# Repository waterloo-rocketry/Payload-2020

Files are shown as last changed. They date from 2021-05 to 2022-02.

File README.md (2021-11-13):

# Waterloo Rocketry Payload 2020/2021

Waterloo Rocketry's Payload hardware and software for the radiation materials analysis experiment

## Contents

PCB Hardware and embedded software for:
* Papa board (power management, logging)
* Mama board (particle detection, noise filtering)
* Protoboard (Mama board prototype board)

Geant4 Monte Carlo simulations have been moved to Payload-Sims

Software for the in-flight controller (see [firmware readme](controller_firmware/README.md))

## Prerequisites

* KiCad
* Geant4
	* See [this link](http://geant4-userdoc.web.cern.ch/geant4-userdoc/UsersGuides/InstallationGuide/html/index.html) for more information on setting up the Geant4 environment
* STM32CubeIDE (see [firmware readme](controller_firmware/README.md))

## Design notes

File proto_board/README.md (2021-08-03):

***************************************Protoboard**************************************

Two parts:

	detector_support:
		* All the supporting infastrucutre, power suppies, logging
	detector_circuit
		* Converts current spike from SiPM to voltage for logging.
			* detector_circuit_LTC6269.sch - Version with LTC6269 op amp. 
			  this amp has been tested and works, but is expensive and consumes 
                          a lot of current, not ideal for flight.
		* detector_circuit_LTC6254 - Version with LTC6264 op amp, previously untested
                  but cheaper and has a significantly lower quiescent current.
		* detector_circuit_alt_LTC6254 - Different version of transimpedance amplifier with 
		  filtering built in. Experimental, but it would be really cool and worth a try. 

Each of the detector circuits connect to the support board with the listed connectors:
* J9 - SIPM_CONN
* J2 - DET_CONN_PWR
* J11 

***********************************Project Overview***********************************

Measuring the radiation detection properties of BNNTs and Metal Oxides.

Radiaiton detection
Scintillator - Lights up when exposed to ionizing radiation
SiPM - Silicon photomultiplier, sensor that counts the number of photons it sees.

Scintillator generates light, SiPM generates a current pulse proportional 
to the magnitude of radiation.

In order to detect and log that current pulse on an MCU we need to
1. Convert the current signal to voltage 
2. Amplify the voltage pulse to increase difference between singal and noise
and make it easier to detect and losses negligible.
3. Extend the length of the signal so the MCU has time to made an ADC conversion.

Detector Circuit Topology:

1. Transimpdance amplifier converts current signal to voltage, amplifies it in a way
to reduce the signal to noise ratio. The main purpose of this board is to fine-tune the 
resistor and capacitor values to optimize the gain on this amplifier.
2. Filter stage to eliminaty high and low frequency noise
3. Second stage amplfication
4. Peak detector to extend signal
5. Voltage follower to ensure signal sampling does not interfere with the peak detector circuit.

Data logging:

After the second stage amplificaiton, the signal line is sent to both the peak detector and a comparator.
The comparator compares the signal to a set baseline voltage value, and if the signal exceeds this amount,
it generates an interrupt. This interrupt is used to tell the MCU when to take an ADC sample from the 
peak detector line. 

Voltage supply:

Because the detector circuit is sensative anlaog circuitry, it runs off a seperate 4.7V line 
from an LDO. The LDO cleans the 5V line to ensure low-noise, as well as seperates the detector
circuit supplies from any noise generated by the switching supplies.

The SiPM requires 36V to operate. This is achieved with a voltage booster paried with an LDO to 
make sure the supply voltage is clean. 

The detector_support circuit is configured to support both a test connection (5V and 12V from the 
bench top supply) as well as battery connections for use in lab testing.

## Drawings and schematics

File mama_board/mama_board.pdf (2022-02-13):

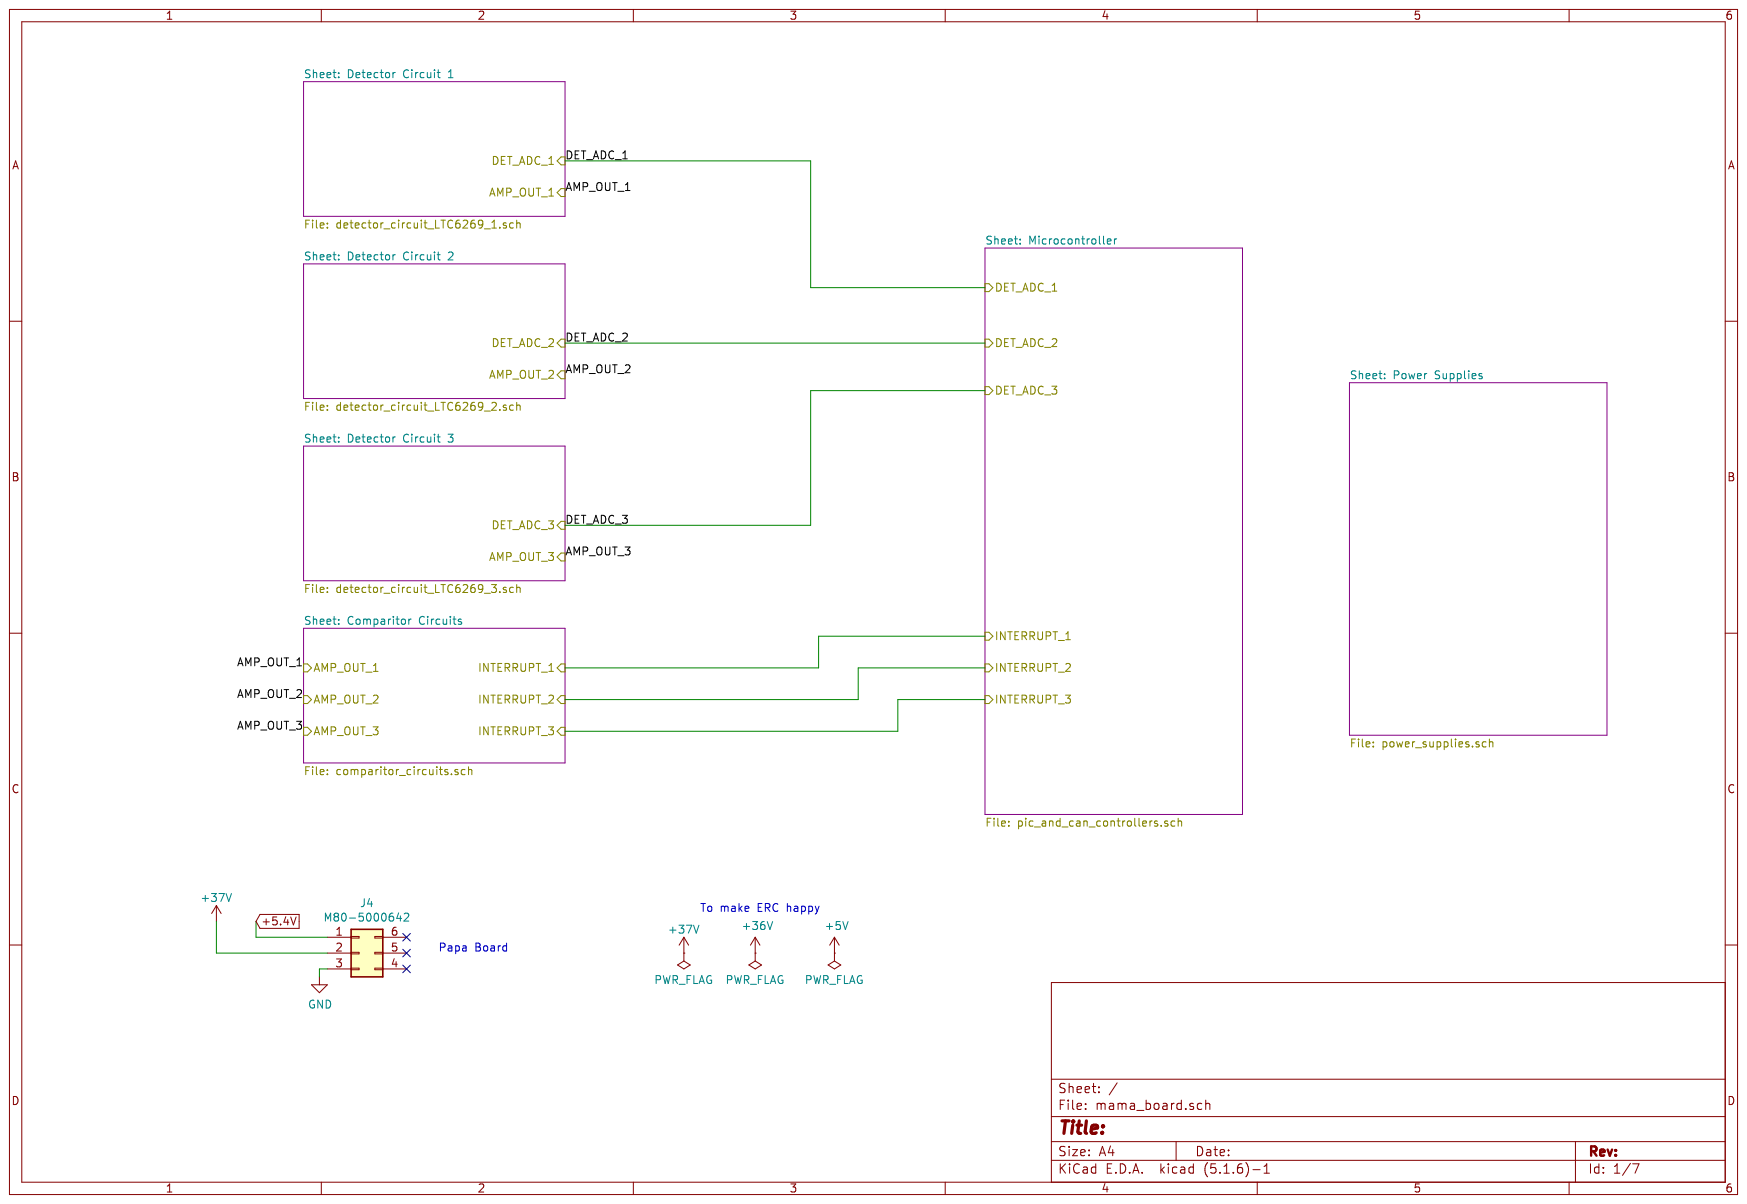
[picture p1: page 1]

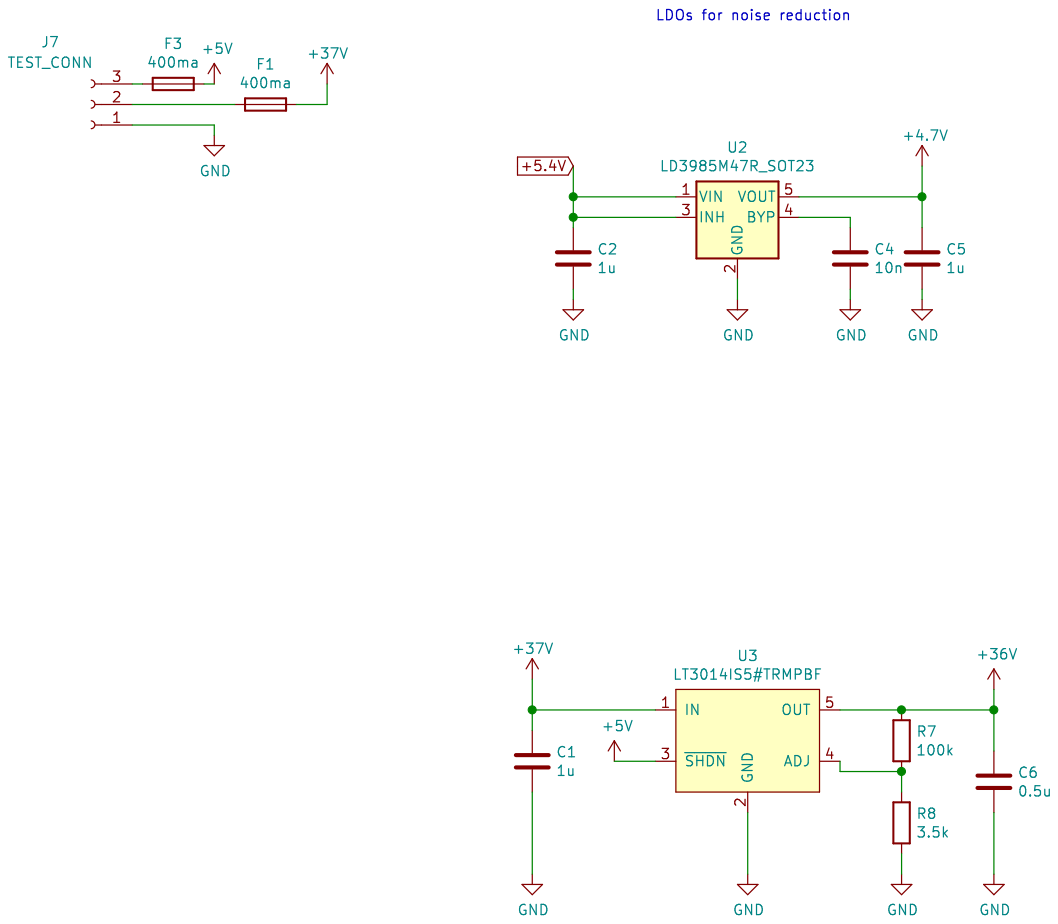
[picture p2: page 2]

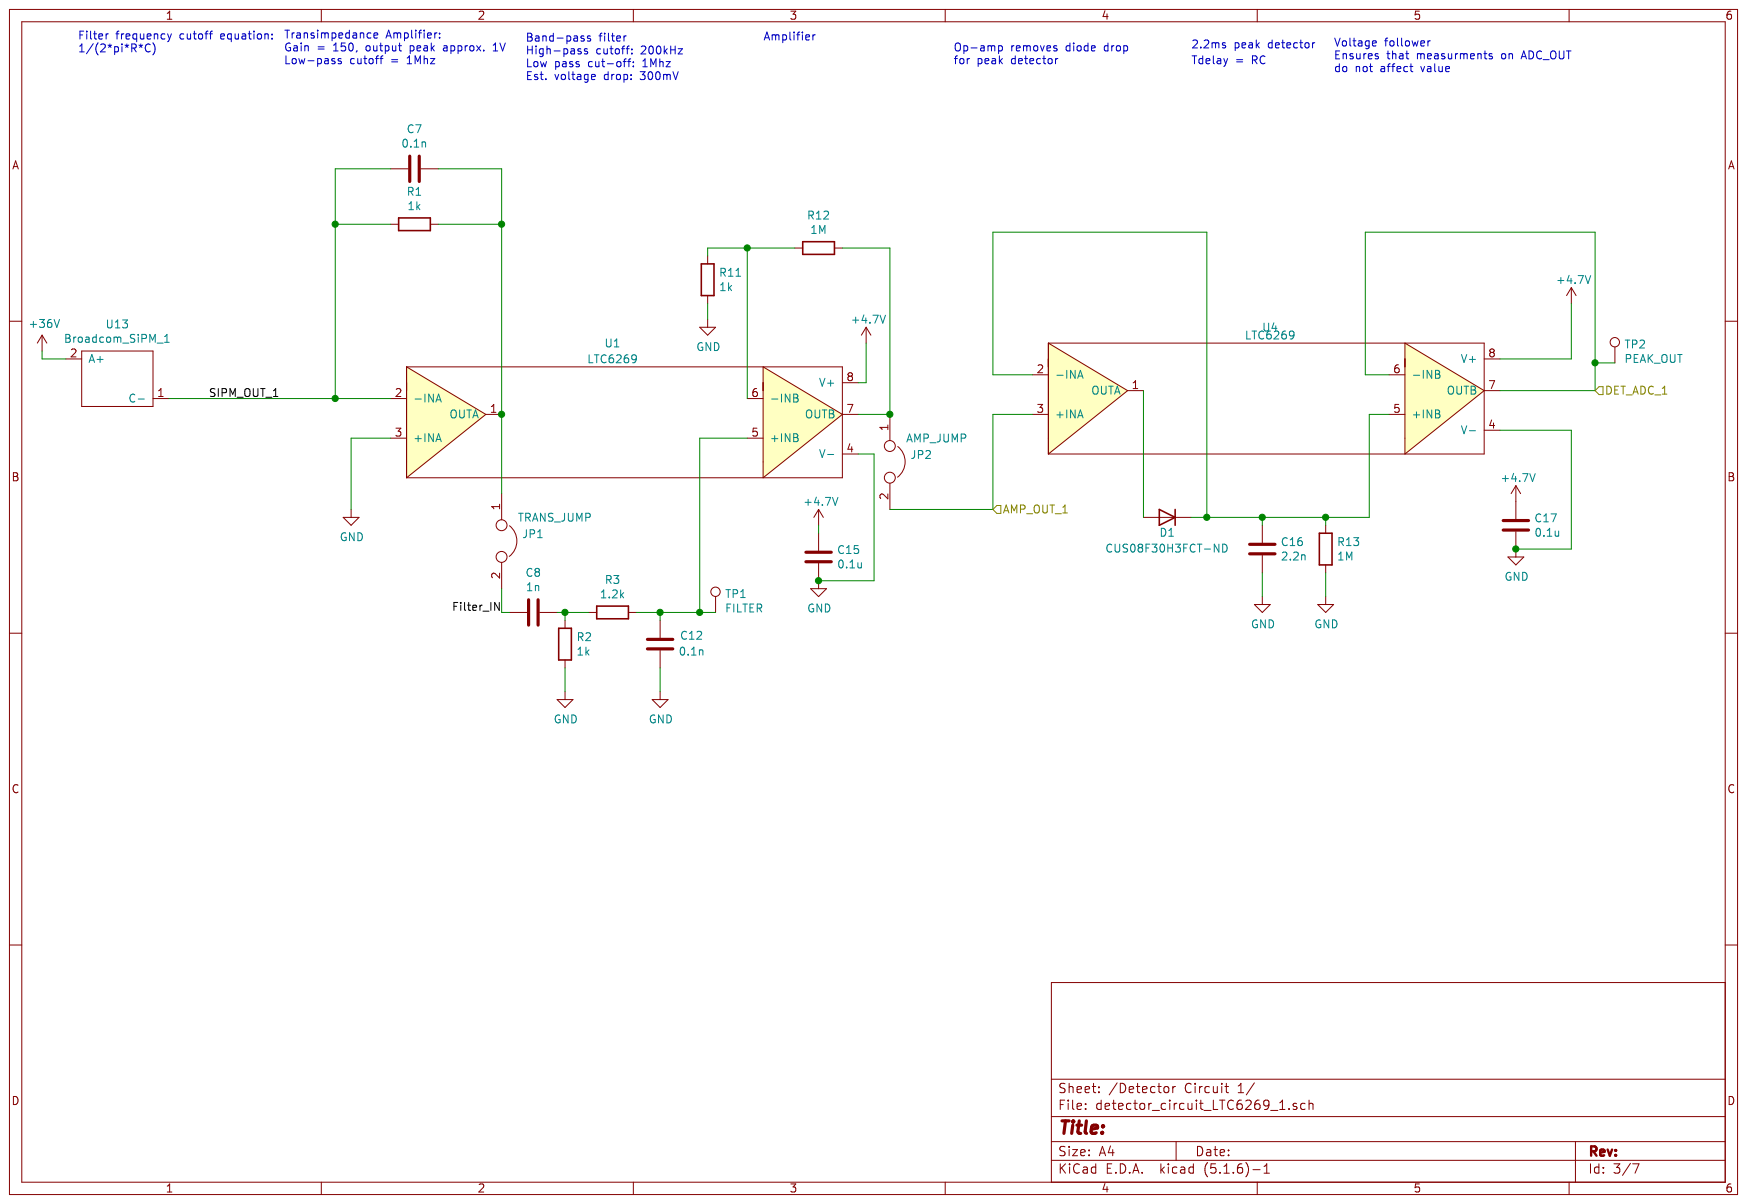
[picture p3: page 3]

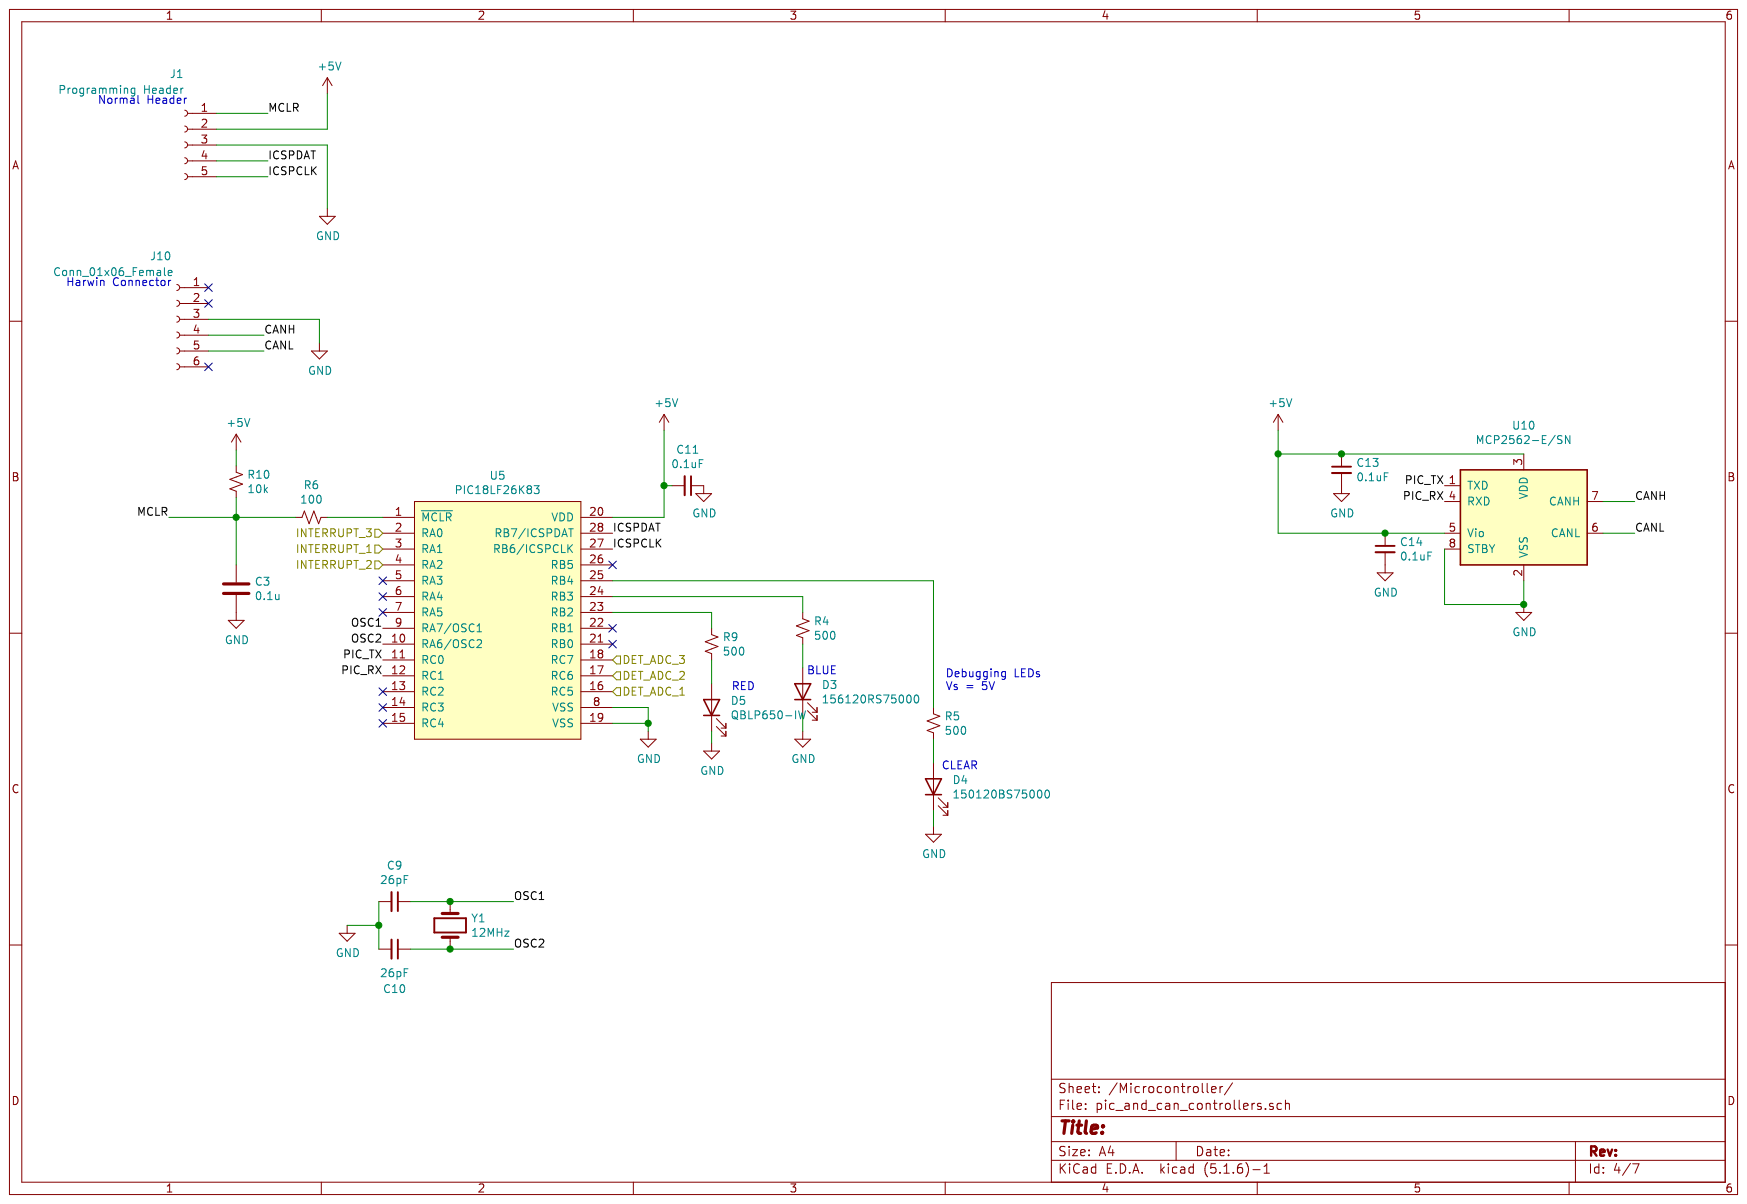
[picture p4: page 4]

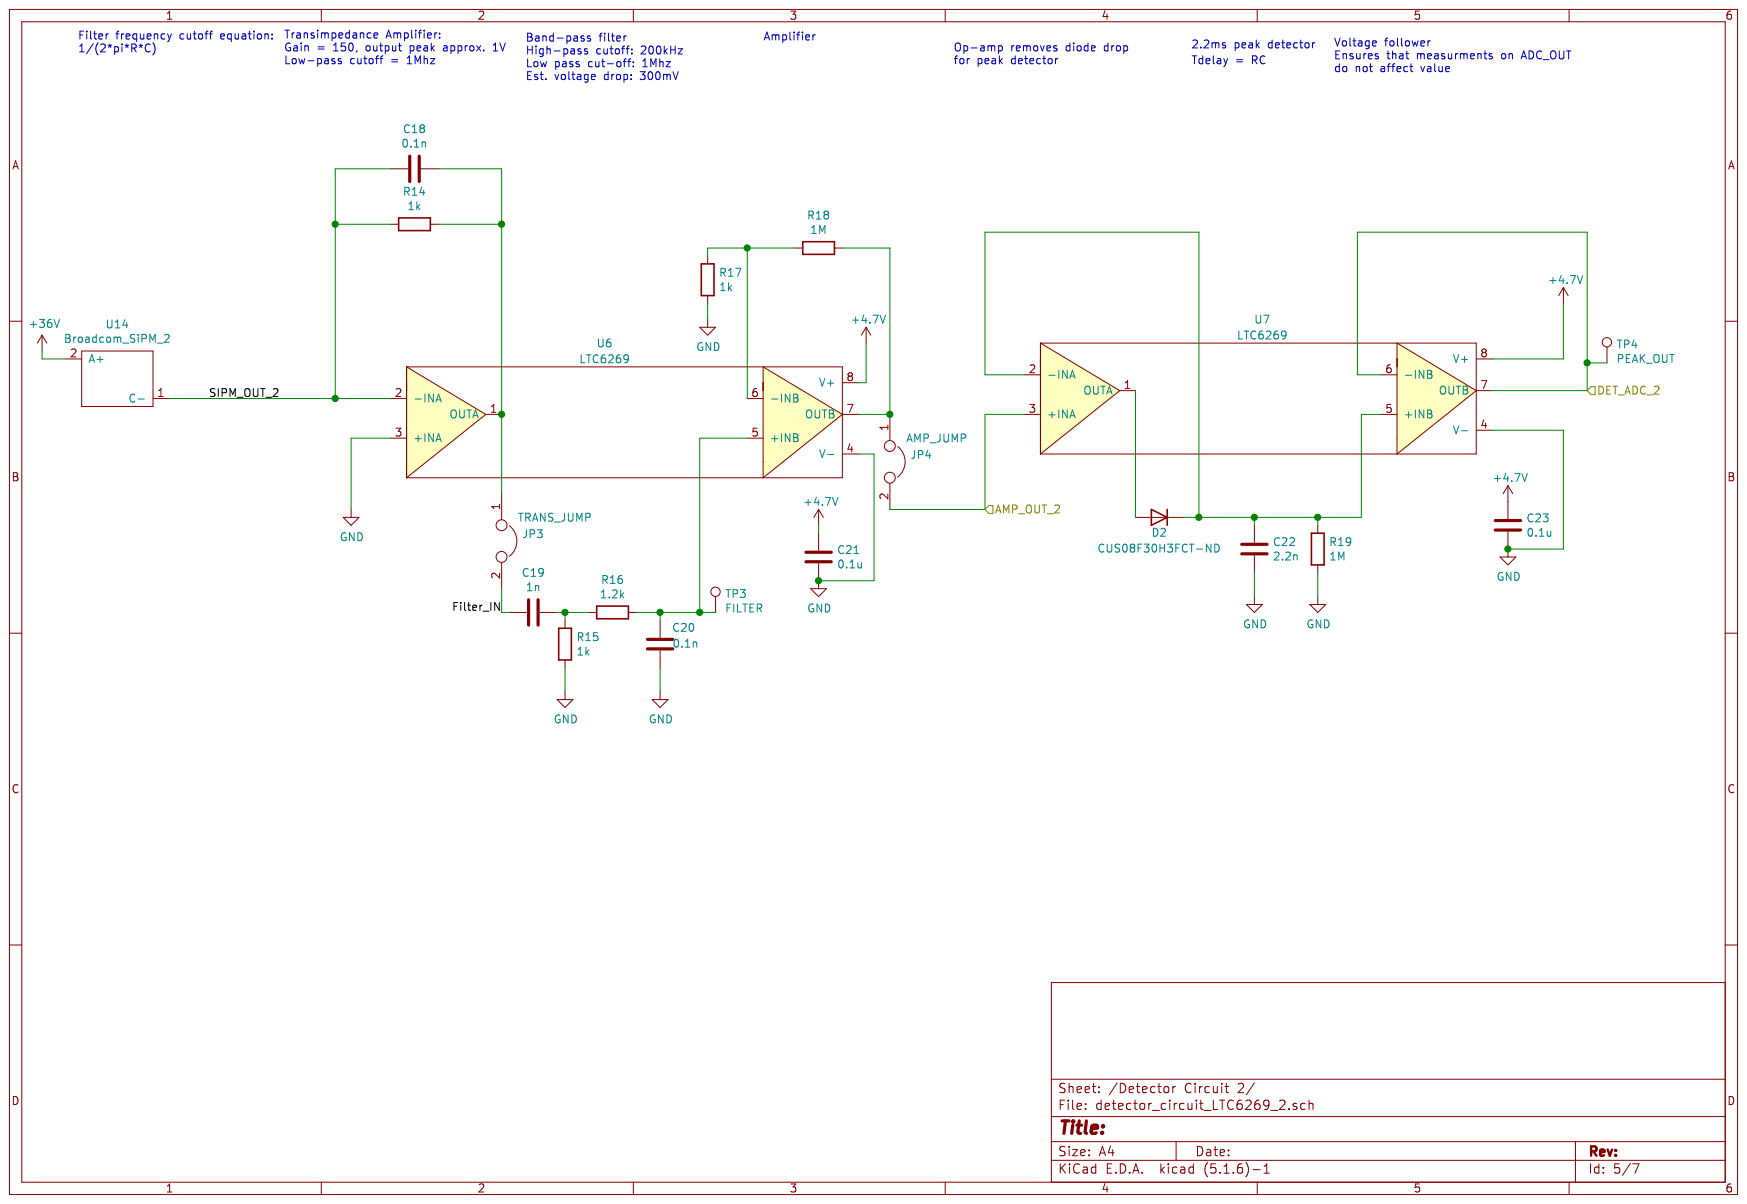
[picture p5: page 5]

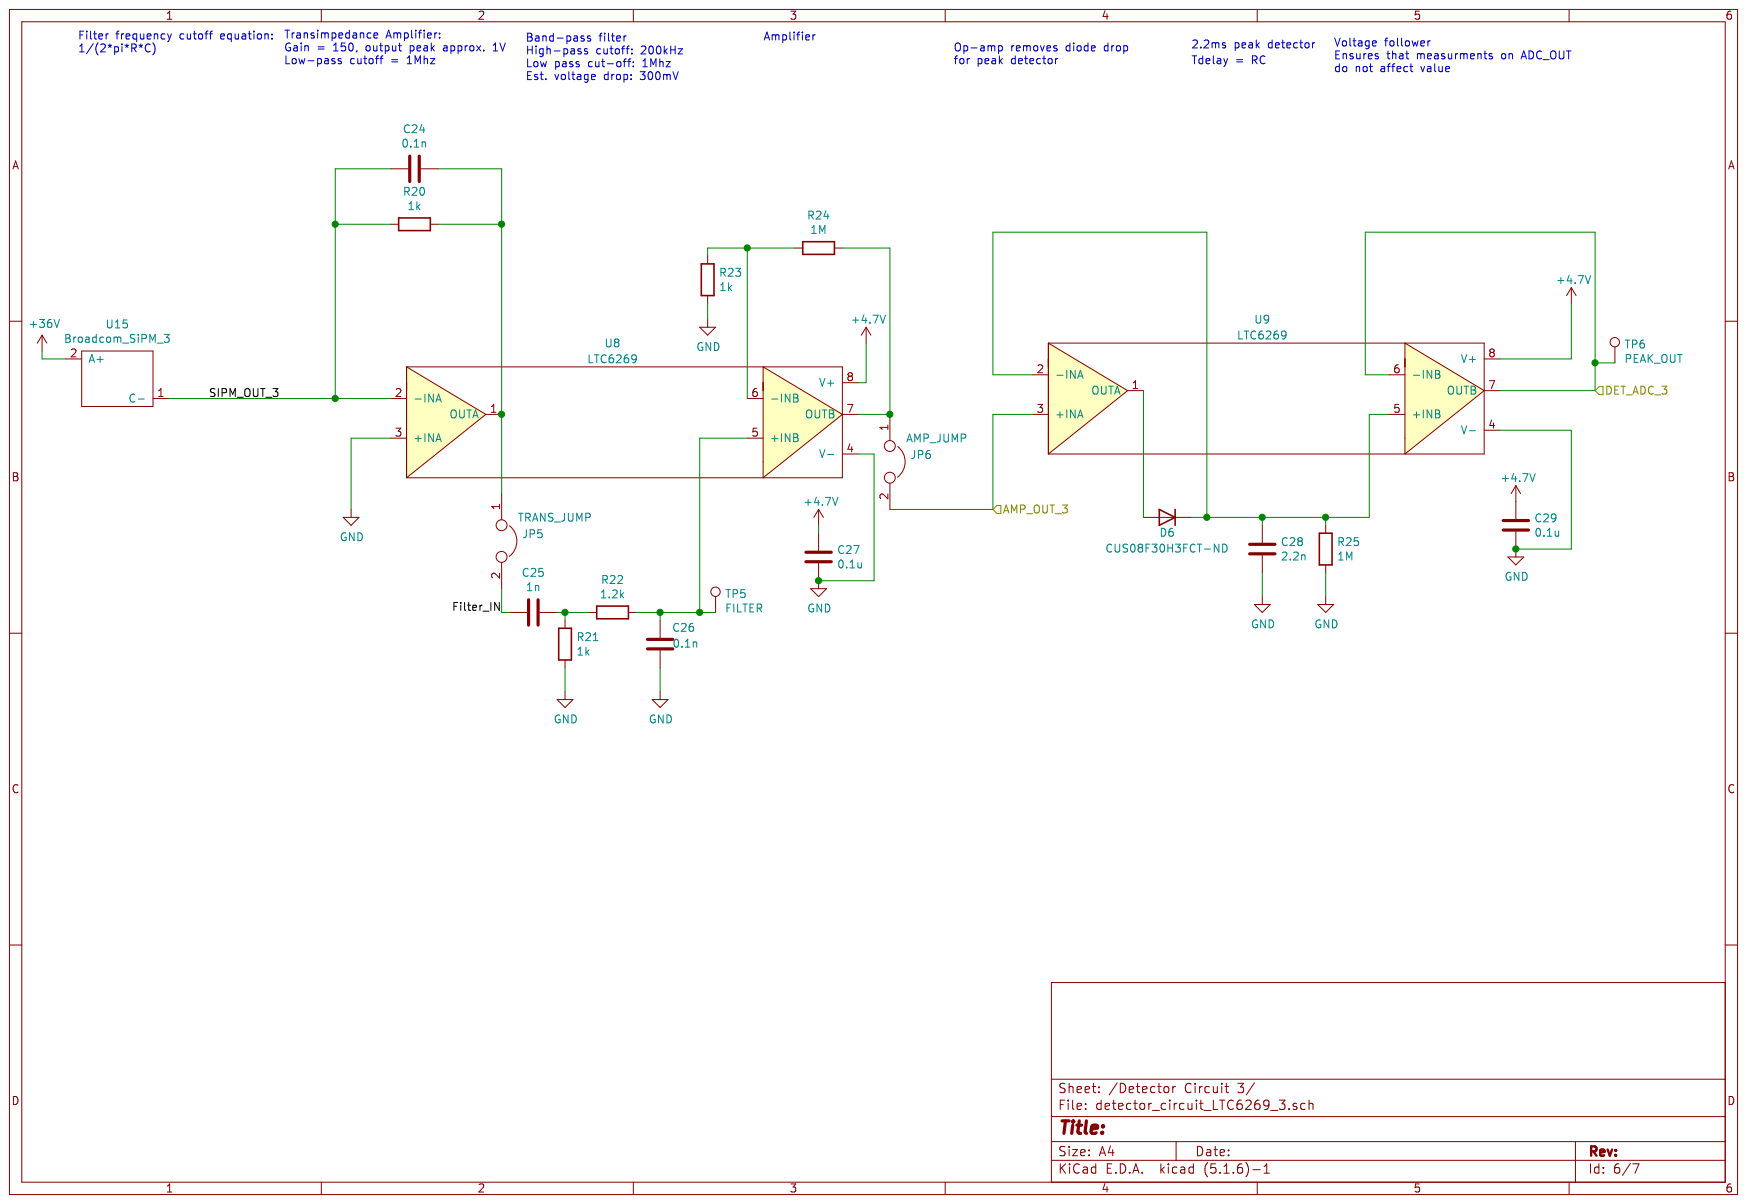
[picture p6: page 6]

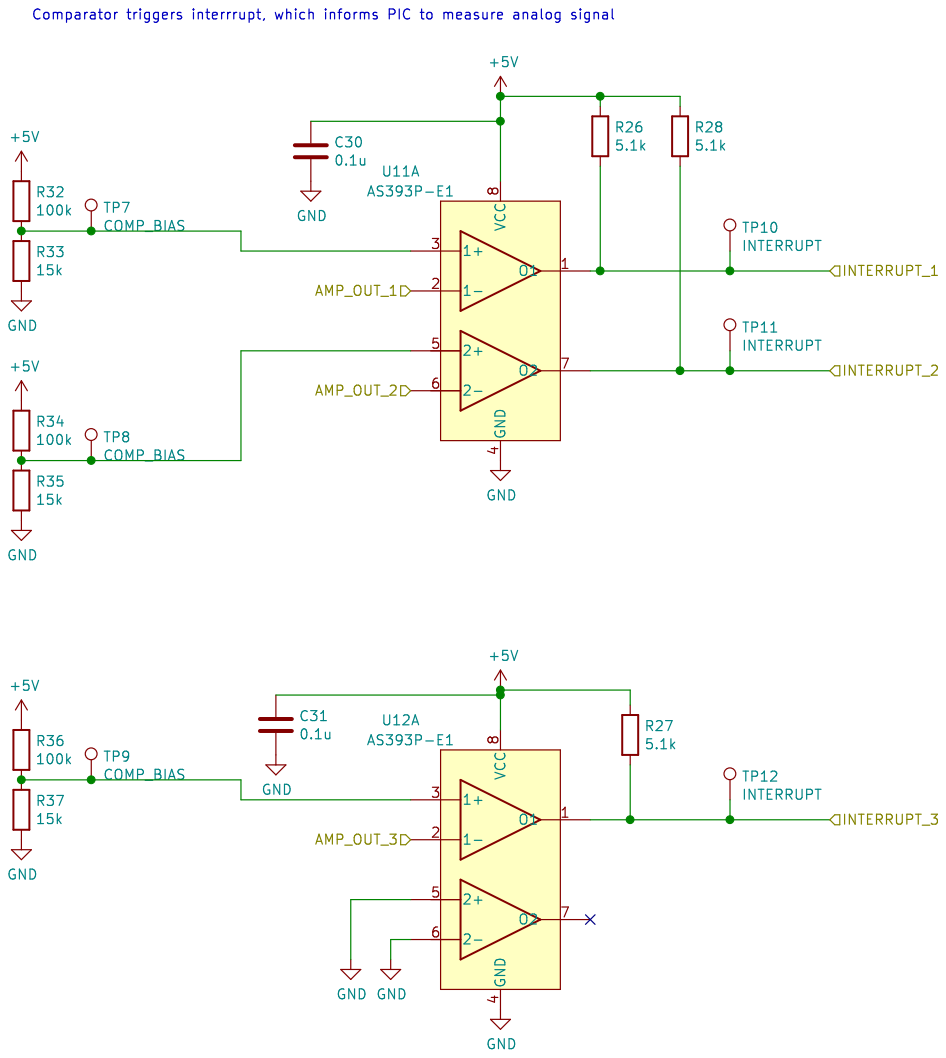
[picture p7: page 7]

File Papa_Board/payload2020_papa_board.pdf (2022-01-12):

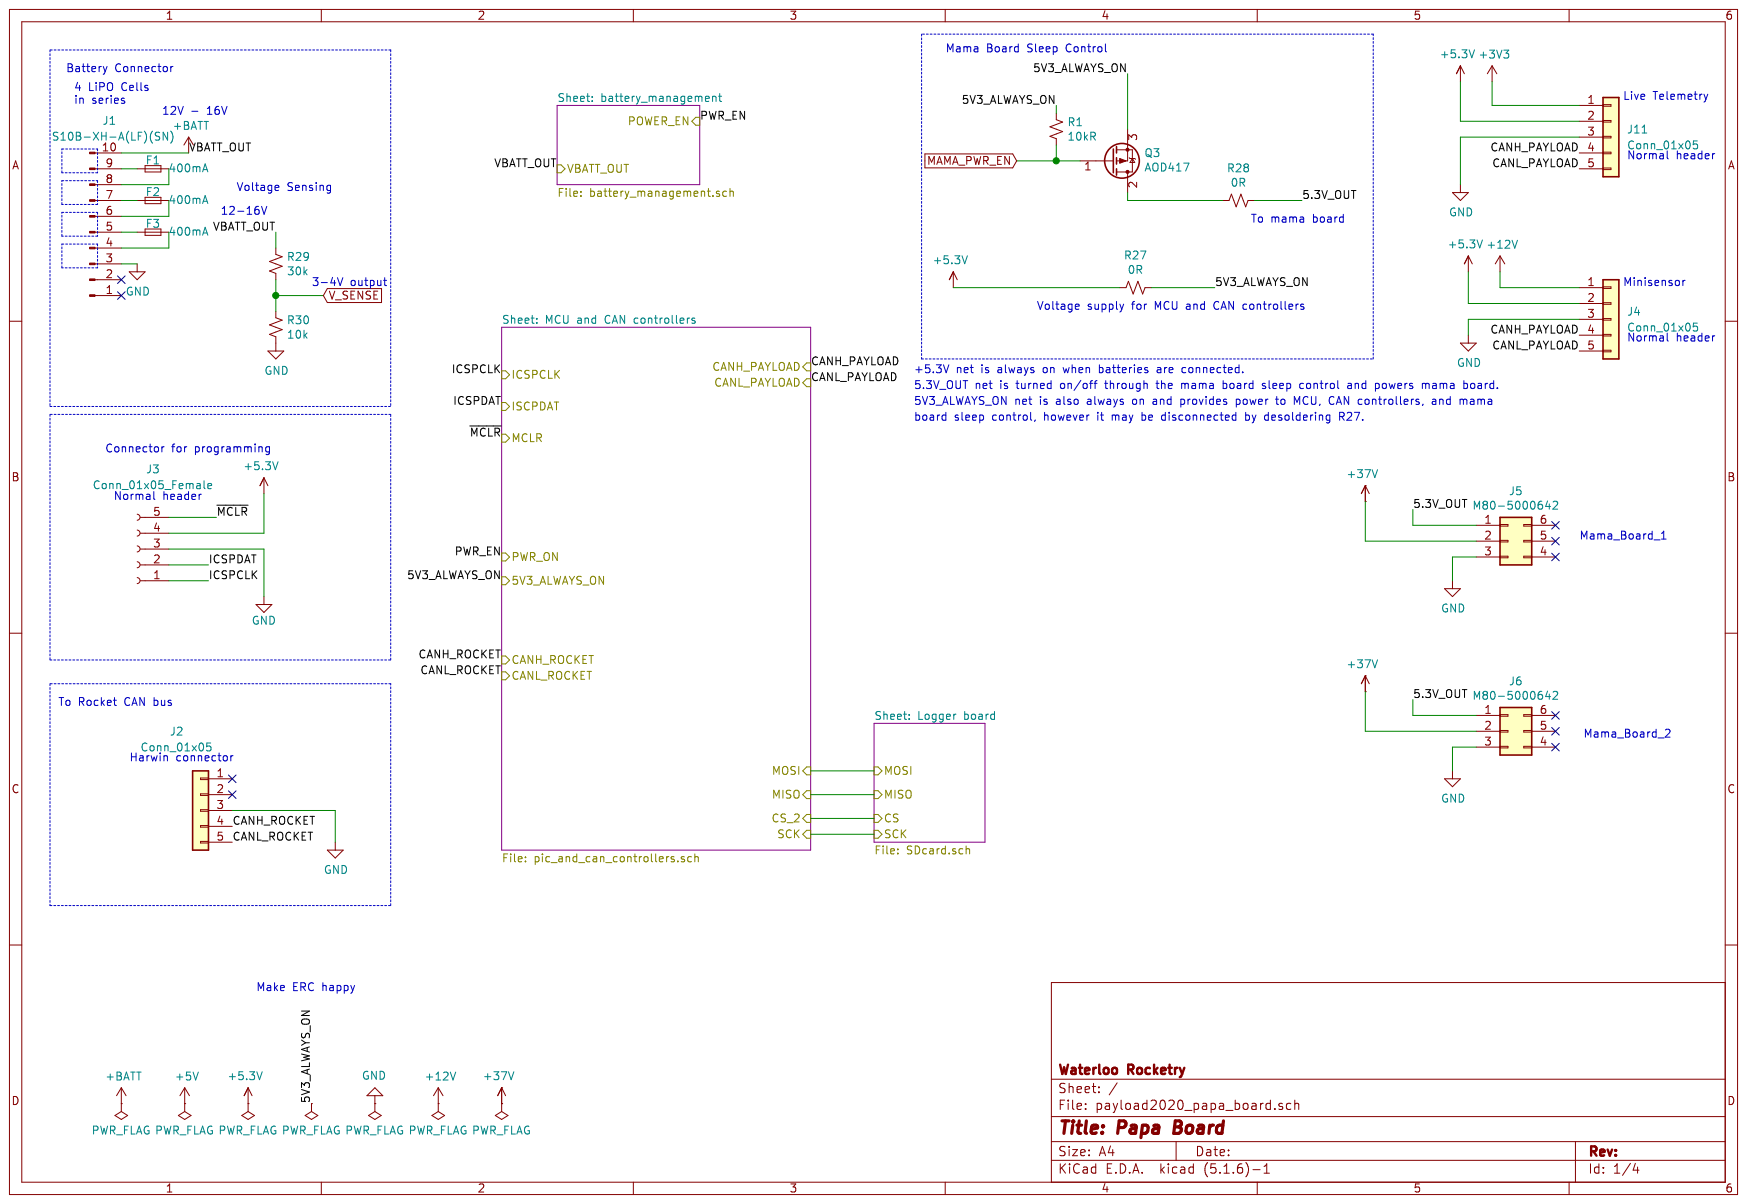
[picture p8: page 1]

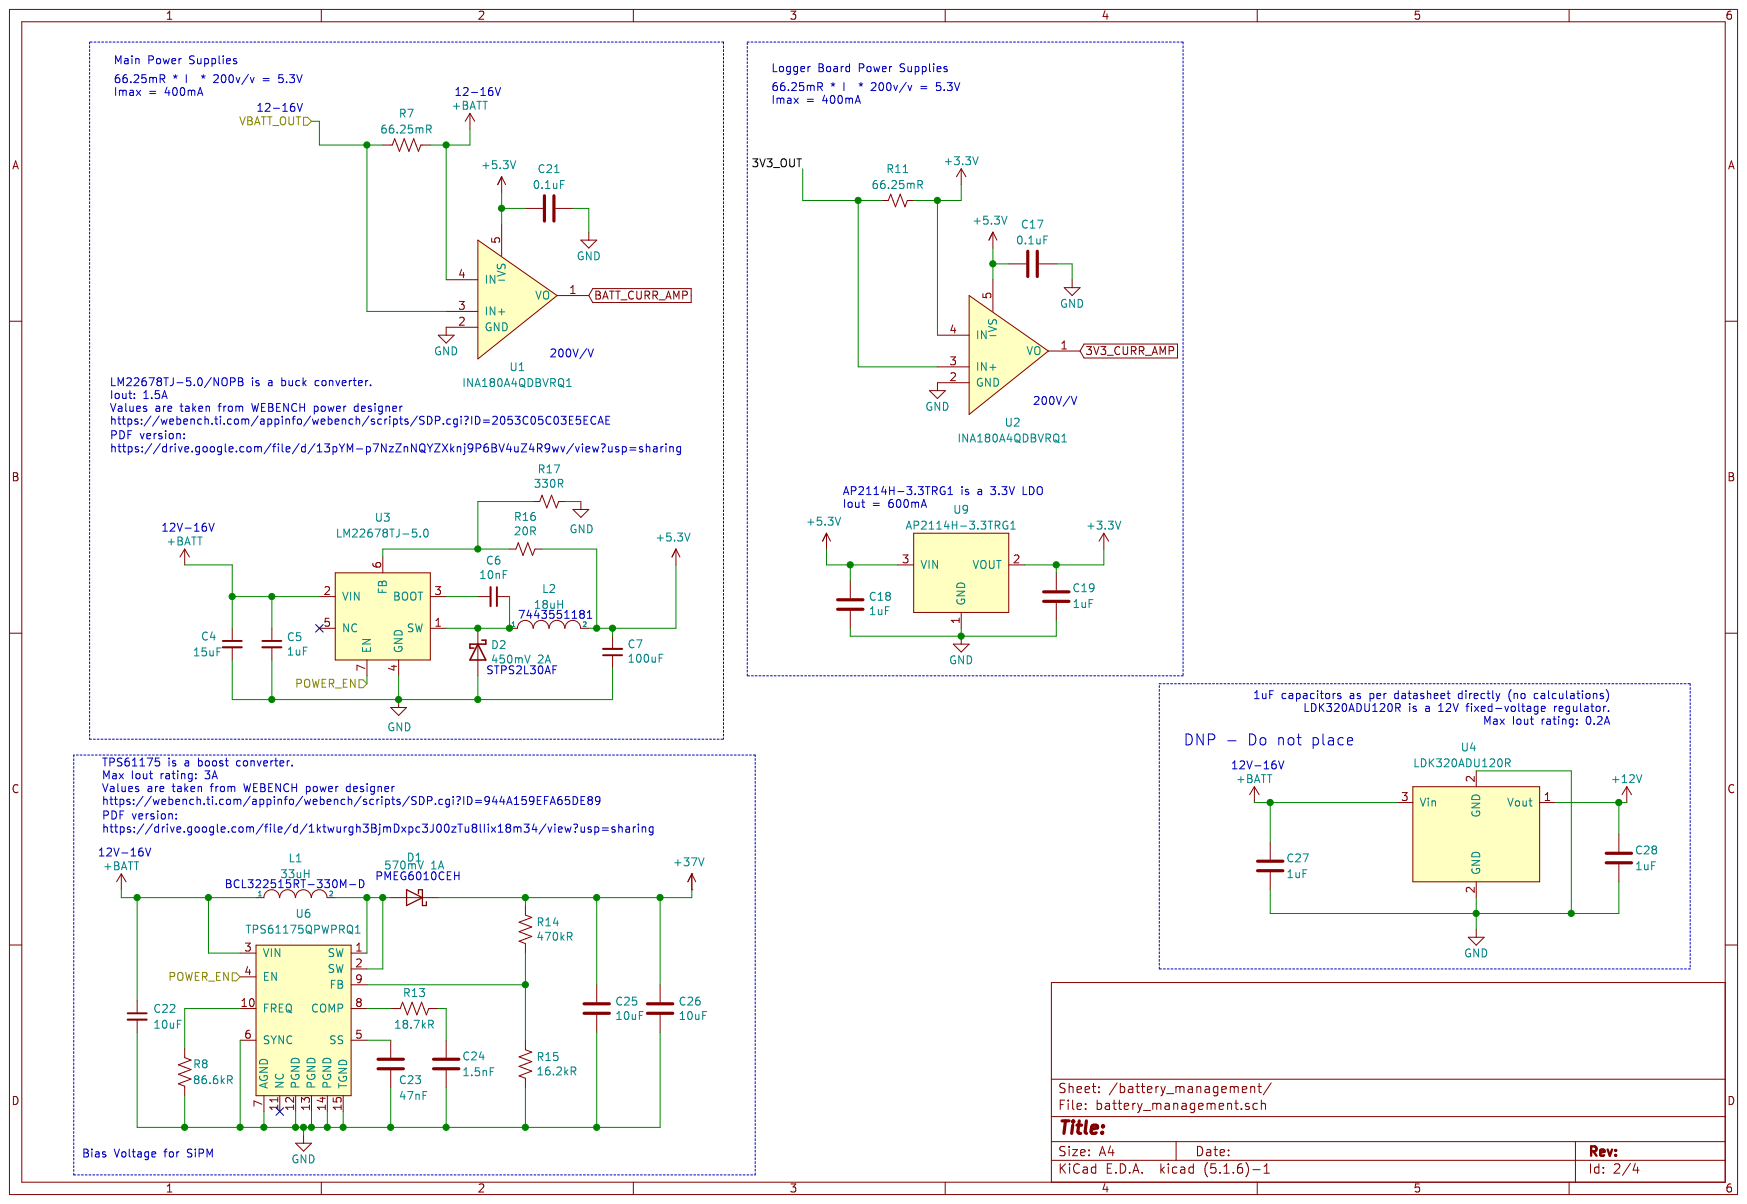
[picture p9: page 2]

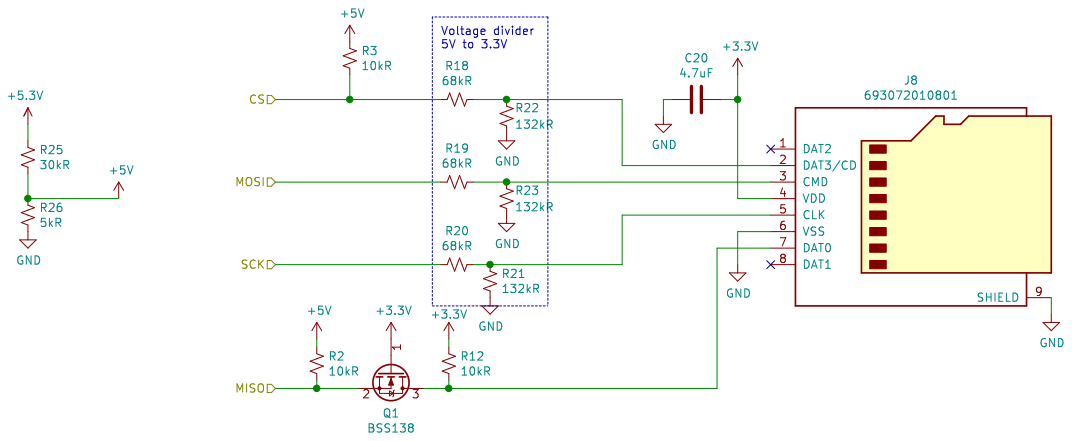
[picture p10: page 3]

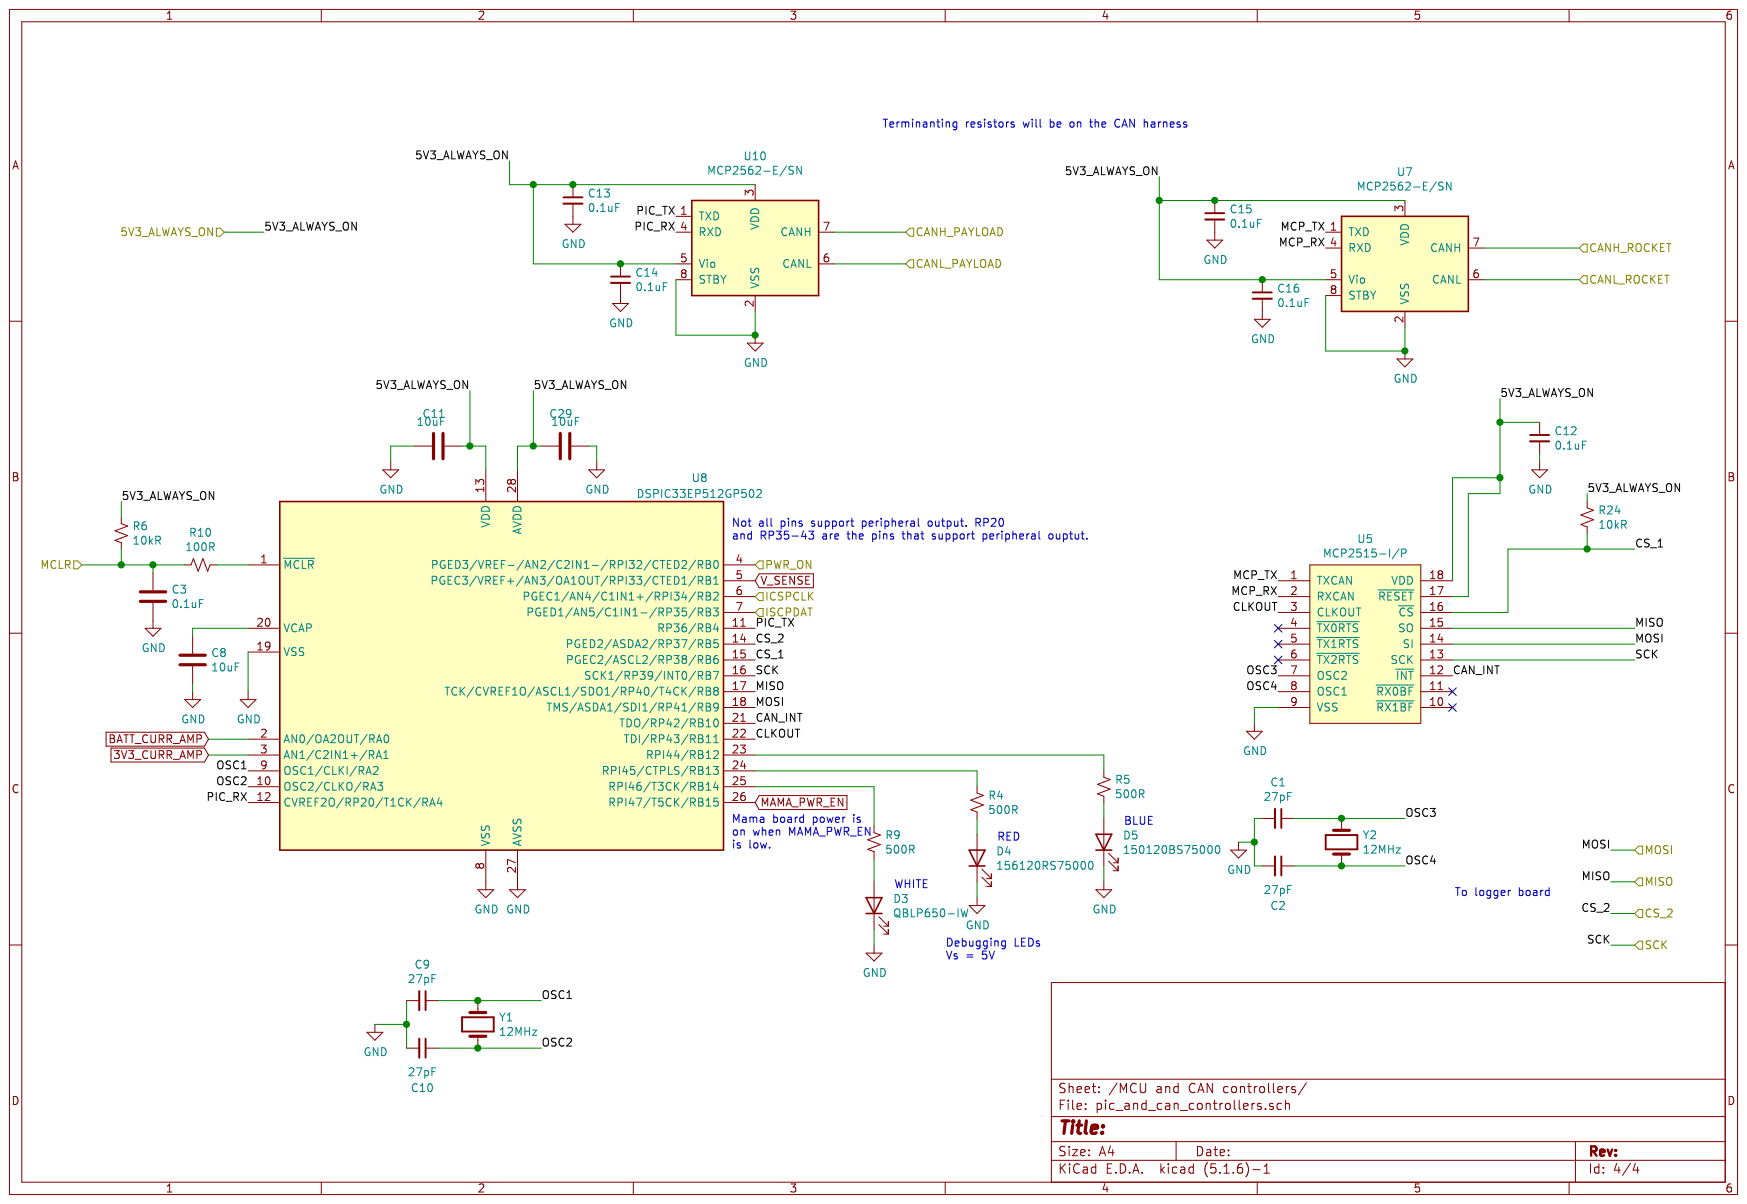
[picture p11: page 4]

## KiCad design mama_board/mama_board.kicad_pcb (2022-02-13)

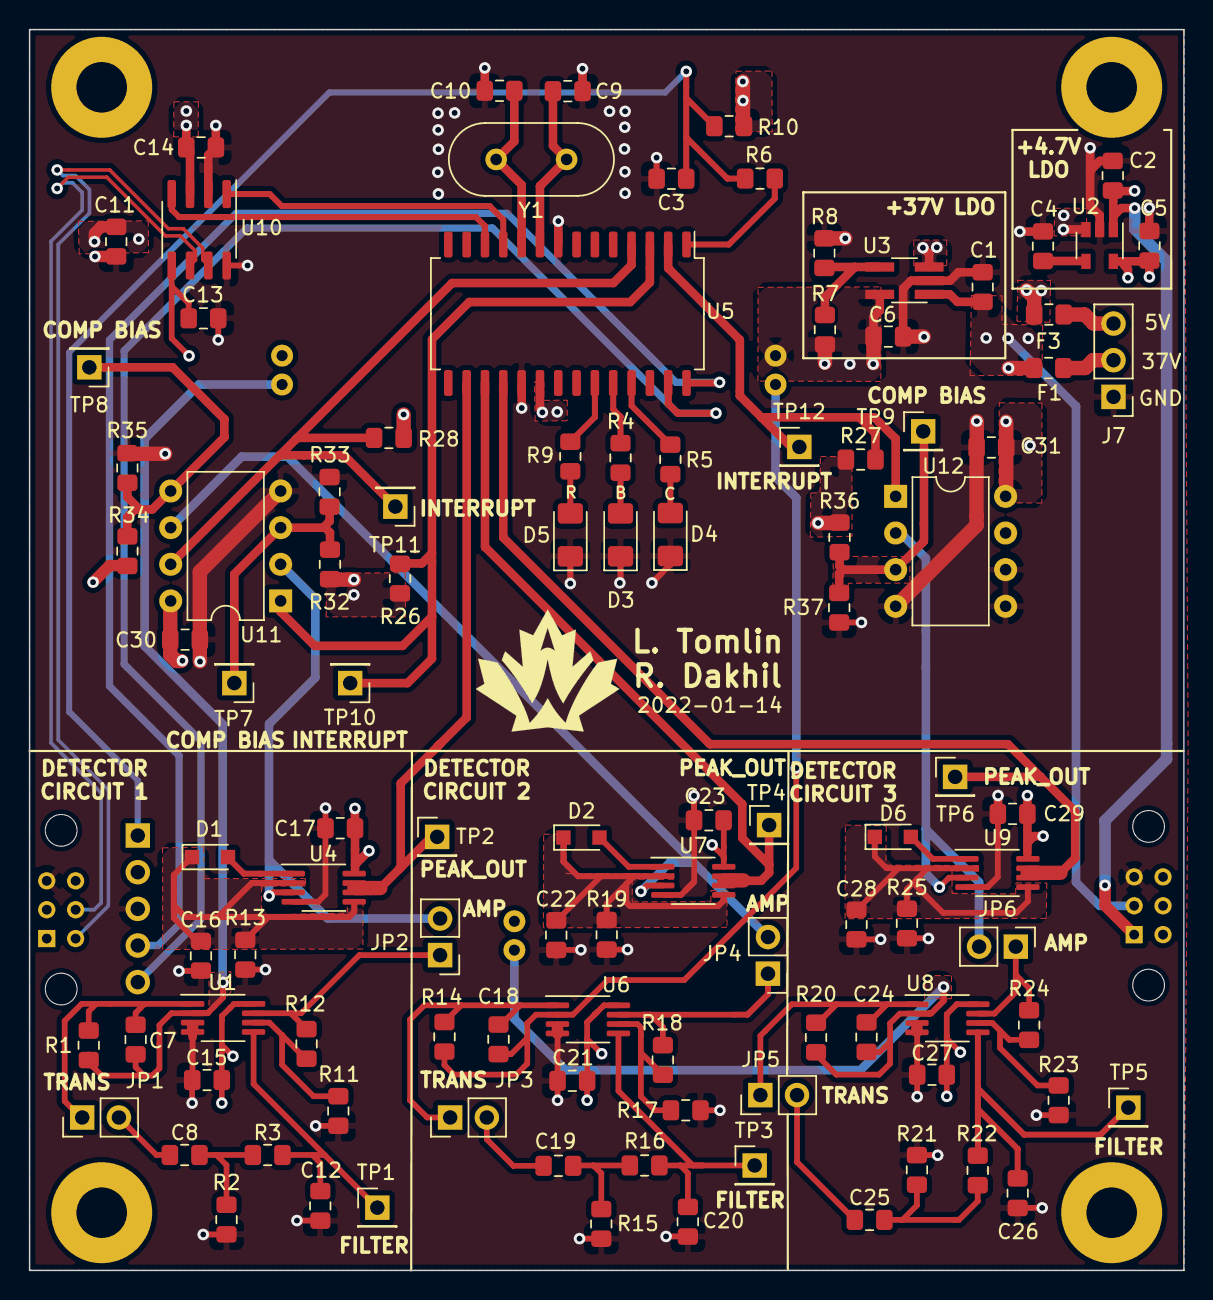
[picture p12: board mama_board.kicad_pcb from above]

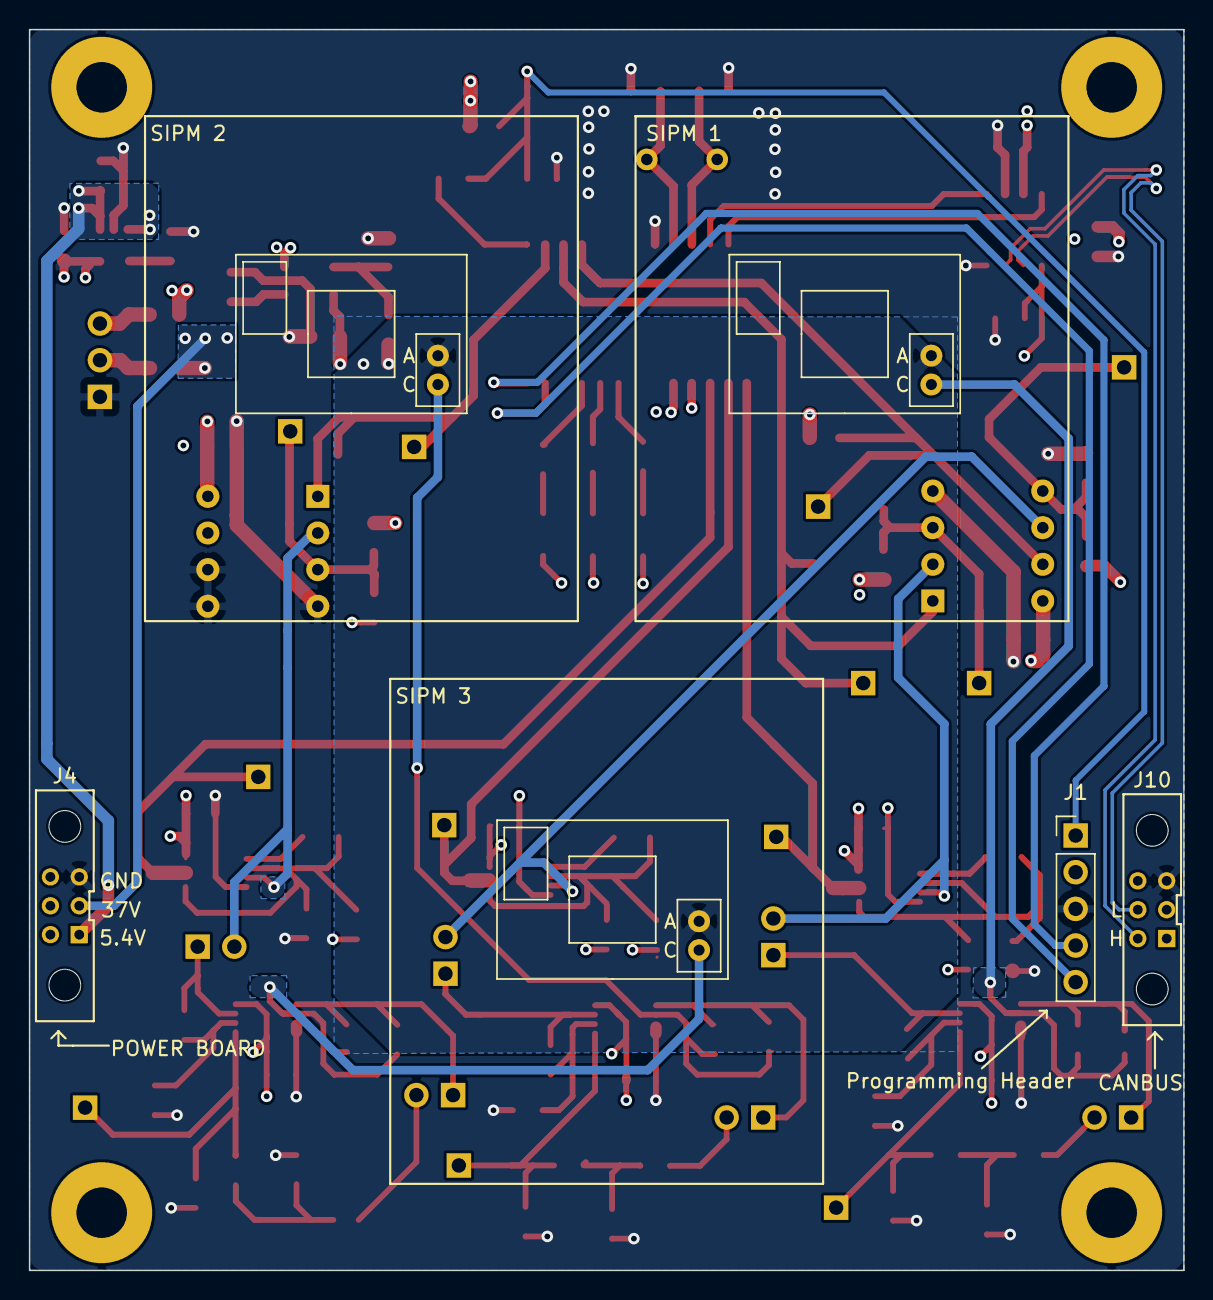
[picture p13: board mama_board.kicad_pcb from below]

Board: 4 copper layers, 80.0 x 86.0 mm, 111 parts (6 on the bottom side), 65 nets.

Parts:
C1, C2, C5: 1u; C_0805_2012Metric_Pad1.15x1.40mm_HandSolder
C3, C15, C17, C21, C23, C27, C29, C30, C31: 0.1u; C_0805_2012Metric_Pad1.15x1.40mm_HandSolder
C4: 10n; C_0805_2012Metric_Pad1.15x1.40mm_HandSolder
C6: 0.5u; C_0805_2012Metric_Pad1.15x1.40mm_HandSolder
C7, C12, C18, C20, C24, C26: 0.1n; C_0805_2012Metric_Pad1.15x1.40mm_HandSolder
C8, C19, C25: 1n; C_0805_2012Metric_Pad1.15x1.40mm_HandSolder
C9, C10: 26pF; C_0805_2012Metric_Pad1.15x1.40mm_HandSolder
C11, C13, C14: 0.1uF; C_0805_2012Metric_Pad1.15x1.40mm_HandSolder
C16, C22, C28: 2.2n; C_0805_2012Metric_Pad1.15x1.40mm_HandSolder
D1, D2, D6: CUS08F30H3FCT-ND; D_SOD-323_HandSoldering
D3: 156120RS75000; D_1206_3216Metric_Pad1.42x1.75mm_HandSolder
D4: 150120BS75000; D_1206_3216Metric_Pad1.42x1.75mm_HandSolder
D5: QBLP650-IW; D_1206_3216Metric_Pad1.42x1.75mm_HandSolder
F1, F3: 400ma; Fuse_0805_2012Metric_Pad1.15x1.40mm_HandSolder
J1: Programming Header; PinHeader_1x05_P2.54mm_Vertical
J4: M80-5000642; connector_Harwin_M80-5000642
J7: TEST_CONN; PinHeader_1x03_P2.54mm_Vertical
J10: Conn_01x06_Female; connector_Harwin_M80-5000642
JP1, JP3, JP5: TRANS_JUMP; PinHeader_1x02_P2.54mm_Vertical
JP2, JP4, JP6: AMP_JUMP; PinHeader_1x02_P2.54mm_Vertical
R1, R2, R11, R14, R15, R17, R20, R21, R23: 1k; R_0805_2012Metric_Pad1.15x1.40mm_HandSolder
R3, R16, R22: 1.2k; R_0805_2012Metric_Pad1.15x1.40mm_HandSolder
R4, R5, R9: 500; R_0805_2012Metric_Pad1.15x1.40mm_HandSolder
R6: 100; R_0805_2012Metric_Pad1.15x1.40mm_HandSolder
R7, R32, R34, R36: 100k; R_0805_2012Metric_Pad1.15x1.40mm_HandSolder
R8: 3.5k; R_0805_2012Metric_Pad1.15x1.40mm_HandSolder
R10: 10k; R_0805_2012Metric_Pad1.15x1.40mm_HandSolder
R12, R13, R18, R19, R24, R25: 1M; R_0805_2012Metric_Pad1.15x1.40mm_HandSolder
R26, R27, R28: 5.1k; R_0805_2012Metric_Pad1.15x1.40mm_HandSolder
R33, R35, R37: 15k; R_0805_2012Metric_Pad1.15x1.40mm_HandSolder
TP1, TP3, TP5: FILTER; PinHeader_1x01_P2.54mm_Vertical
TP2, TP4, TP6: PEAK_OUT; PinHeader_1x01_P2.54mm_Vertical
TP7, TP8, TP9: COMP_BIAS; PinHeader_1x01_P2.54mm_Vertical
TP10, TP11, TP12: INTERRUPT; PinHeader_1x01_P2.54mm_Vertical
U1, U4, U6, U7, U8, U9: LTC6269; MSOP-8_3x3mm_P0.65mm
U2: LD3985M47R_SOT23; SOT-23-5
U3: LT3014IS5#TRMPBF; TSOT-23-5_HandSoldering
U5: PIC18LF26K83; SOIC-28W_7.5x18.7mm_P1.27mm
U10: MCP2562-E/SN; SOIC-8_3.9x4.9mm_P1.27mm
U11, U12: AS393P-E1; DIP-8_W7.62mm
U13: Broadcom_SiPM_1; BROADCOM_SiPM
U14: Broadcom_SiPM_2; BROADCOM_SiPM
U15: Broadcom_SiPM_3; BROADCOM_SiPM
Y1: 12MHz; Crystal_HC49-4H_Vertical

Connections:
+4.7V: C5.1, C15.1, C17.1, C21.1, C23.1, C27.1, C29.1, U1.8, U2.5, U4.8, U6.8, U7.8, U8.8, U9.8
+5.4V: C2.1, J4.1, U2.1, U2.3
+5V: C11.2, C13.1, C14.1, C30.1, C31.1, F3.1, J1.2, R10.1, R26.1, R27.1, R28.1, R32.1, R34.1, R36.1, U3.3, U5.20, U10.3, U10.5, U11.8, U12.8
+36V: C6.1, R7.1, U3.5, U13.2, U14.2, U15.2
+37V: C1.1, F1.1, J4.2, U3.1
/AMP_OUT_1: JP2.2, U4.3, U11.2
/AMP_OUT_2: JP4.2, U7.3, U11.6
/AMP_OUT_3: JP6.2, U9.3, U12.2
/Comparitor Circuits/INTERRUPT_1: R26.2, TP10.1, U5.3, U11.1
/Comparitor Circuits/INTERRUPT_2: R28.2, TP11.1, U5.4, U11.7
/Comparitor Circuits/INTERRUPT_3: R27.2, TP12.1, U5.2, U12.1
/DET_ADC_1: TP2.1, U4.6, U4.7, U5.16
/DET_ADC_2: TP4.1, U5.17, U7.6, U7.7
/DET_ADC_3: TP6.1, U5.18, U9.6, U9.7
/Detector Circuit 1/Filter_IN: C8.2, JP1.2
/Detector Circuit 1/SIPM_OUT_1: C7.2, R1.2, U1.2, U13.1
/Detector Circuit 2/Filter_IN: C19.2, JP3.2
/Detector Circuit 2/SIPM_OUT_2: C18.2, R14.2, U6.2, U14.1
/Detector Circuit 3/Filter_IN: C25.2, JP5.2
/Detector Circuit 3/SIPM_OUT_3: C24.2, R20.2, U8.2, U15.1
/Microcontroller/CANH: J10.4, U10.7
/Microcontroller/CANL: J10.5, U10.6
/Microcontroller/ICSPCLK: J1.5, U5.27
/Microcontroller/ICSPDAT: J1.4, U5.28
/Microcontroller/MCLR: C3.1, J1.1, R6.2, R10.2
/Microcontroller/OSC1: C9.1, U5.9, Y1.1
/Microcontroller/OSC2: C10.1, U5.10, Y1.2
/Microcontroller/PIC_RX: U5.12, U10.4
/Microcontroller/PIC_TX: U5.11, U10.1
GND: C1.2, C2.2, C3.2, C4.2, C5.2, C6.2, C9.2, C10.2, C11.1, C12.1, C13.2, C14.2, C15.2, C16.2, C17.2, C20.1, C21.2, C22.2, C23.2, C26.1, C27.2, C28.2, C29.2, C30.2, C31.2, D3.1, D4.1, D5.1, J1.3, J4.3, J7.1, J10.3, R2.2, R8.2, R11.2, R13.2, R15.2, R17.2, R19.2, R21.2, R23.2, R25.2, R33.2, R35.2, R37.2, U1.3, U1.4, U2.2, U3.2, U4.4, U5.8, U5.19, U6.3, U6.4, U7.4, U8.3, U8.4, U9.4, U10.2, U10.8, U11.4, U12.4, U12.5, U12.6
unnamed: C4.1, U2.4
unnamed: C7.1, JP1.1, R1.1, U1.1
unnamed: C8.1, R2.1, R3.2
unnamed: C12.2, R3.1, TP1.1, U1.5
unnamed: C16.1, D1.1, R13.1, U4.2, U4.5
unnamed: C18.1, JP3.1, R14.1, U6.1
unnamed: C19.1, R15.1, R16.2
unnamed: C20.2, R16.1, TP3.1, U6.5
unnamed: C22.1, D2.1, R19.1, U7.2, U7.5
unnamed: C24.1, JP5.1, R20.1, U8.1
unnamed: C25.1, R21.1, R22.2
unnamed: C26.2, R22.1, TP5.1, U8.5
unnamed: C28.1, D6.1, R25.1, U9.2, U9.5
unnamed: D1.2, U4.1
unnamed: D2.2, U7.1
unnamed: D3.2, R4.2
unnamed: D4.2, R5.2
unnamed: D5.2, R9.2
unnamed: D6.2, U9.1
unnamed: F1.2, J7.2
unnamed: F3.2, J7.3
unnamed: JP2.1, R12.1, U1.7
unnamed: JP4.1, R18.1, U6.7
unnamed: JP6.1, R24.1, U8.7
unnamed: R4.1, U5.24
unnamed: R5.1, U5.25
unnamed: R6.1, U5.1
unnamed: R7.2, R8.1, U3.4
unnamed: R9.1, U5.23
unnamed: R11.1, R12.2, U1.6
unnamed: R17.1, R18.2, U6.6
unnamed: R23.1, R24.2, U8.6
unnamed: R32.2, R33.1, TP7.1, U11.3
unnamed: R34.2, R35.1, TP8.1, U11.5
unnamed: R36.2, R37.1, TP9.1, U12.3

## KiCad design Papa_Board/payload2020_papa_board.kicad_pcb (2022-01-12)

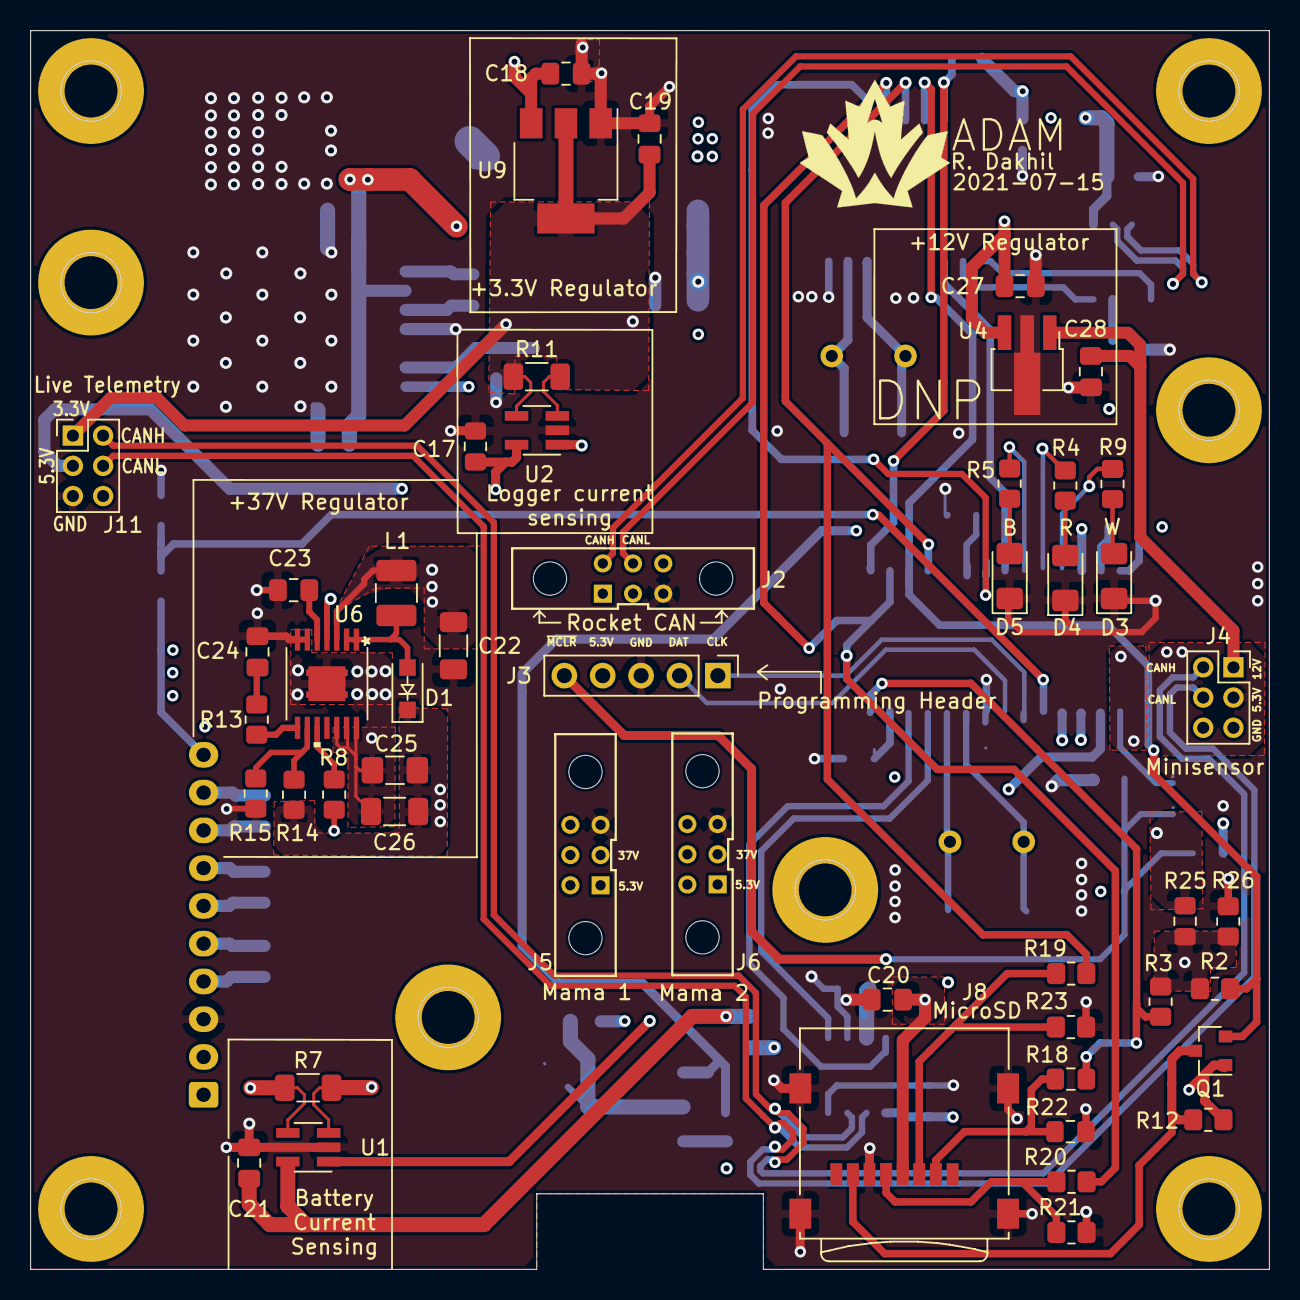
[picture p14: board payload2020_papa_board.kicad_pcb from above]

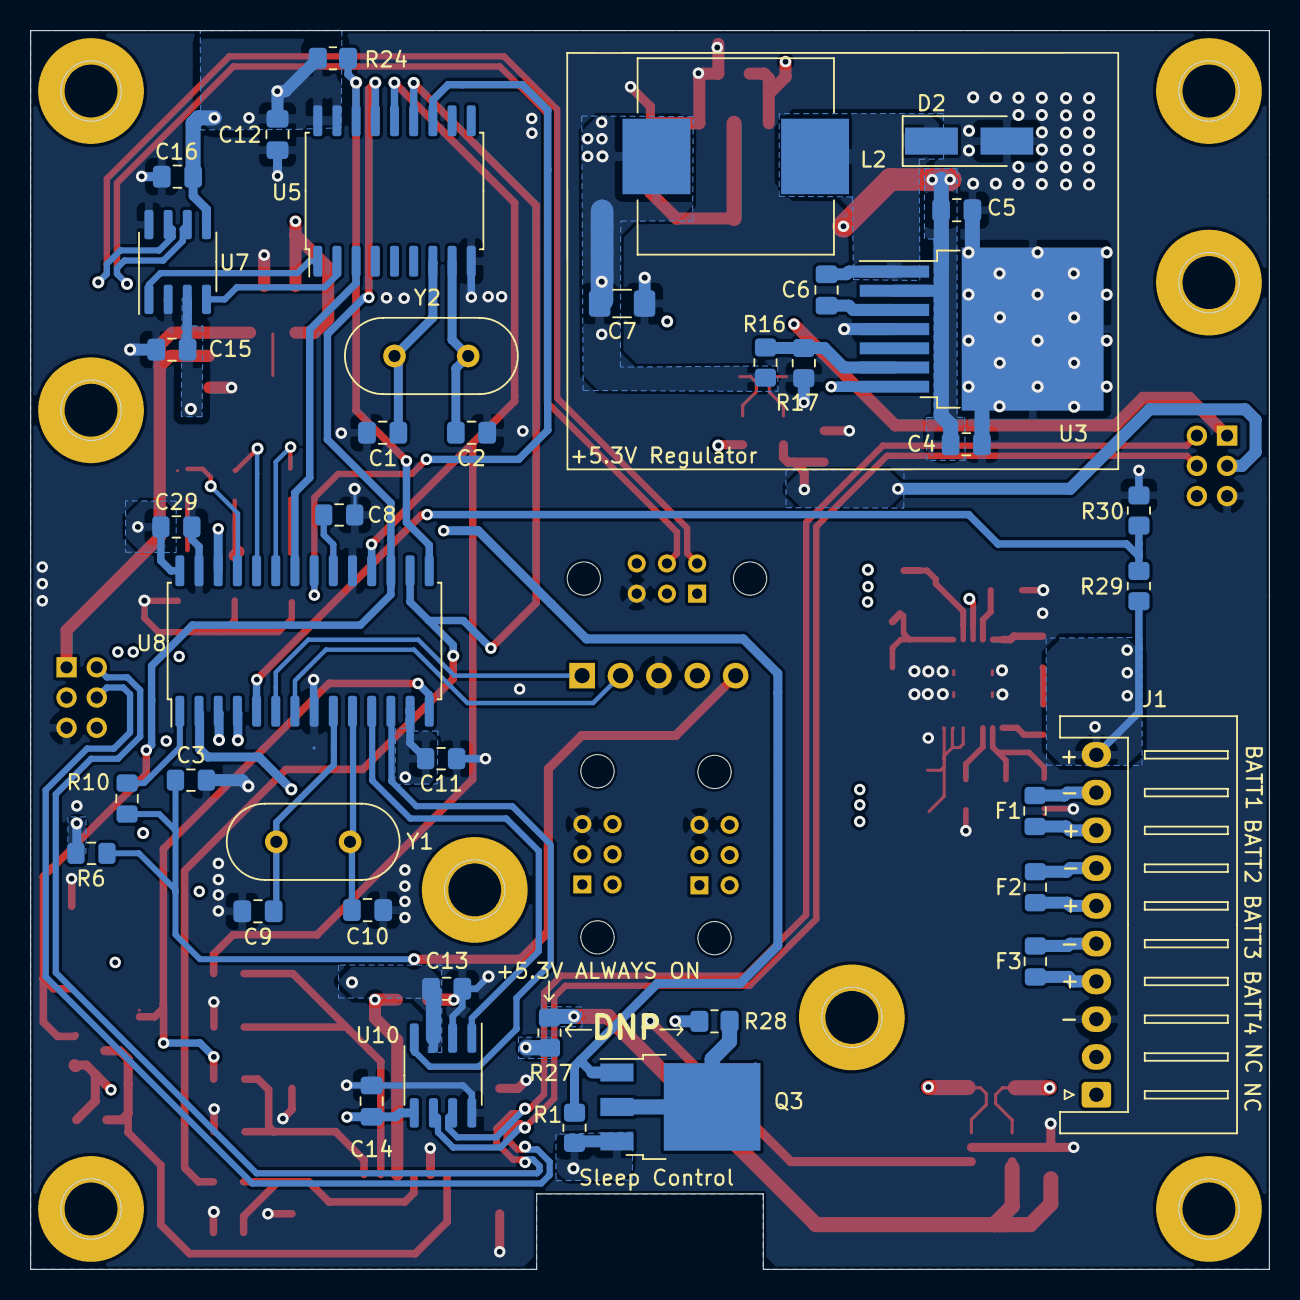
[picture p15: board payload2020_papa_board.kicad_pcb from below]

Board: 4 copper layers, 82.0 x 82.0 mm, 91 parts (41 on the bottom side), 65 nets.

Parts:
C1, C2, C9, C10: 27pF; C_0805_2012Metric_Pad1.18x1.45mm_HandSolder
C3, C17: 0.1uF; C_0805_2012Metric_Pad1.15x1.40mm_HandSolder
C4: 15uF; C_0805_2012Metric_Pad1.18x1.45mm_HandSolder
C5, C18, C19, C27, C28: 1uF; C_0805_2012Metric_Pad1.18x1.45mm_HandSolder
C6: 10nF; C_0805_2012Metric_Pad1.18x1.45mm_HandSolder
C7: 100uF; C_1206_3216Metric_Pad1.42x1.75mm_HandSolder
C8, C11, C29: 10uF; C_0805_2012Metric_Pad1.15x1.40mm_HandSolder
C12, C13, C14, C15, C16, C21: 0.1uF; C_0805_2012Metric_Pad1.18x1.45mm_HandSolder
C20: 4.7uF; C_0805_2012Metric_Pad1.18x1.45mm_HandSolder
C22, C26: 10uF; C_1206_3216Metric_Pad1.33x1.80mm_HandSolder
C23: 47nF; C_0805_2012Metric_Pad1.18x1.45mm_HandSolder
C24: 1.5nF; C_0805_2012Metric_Pad1.18x1.45mm_HandSolder
C25: 10uF; C_1206_3216Metric_Pad1.42x1.75mm_HandSolder
D1: 570mV 1A; D_SOD-123F
D2: 450mV 2A; D_SMA_Handsoldering
D3: QBLP650-IW; LED_1206_3216Metric_Pad1.42x1.75mm_HandSolder
D4: 156120RS75000; LED_1206_3216Metric_Pad1.42x1.75mm_HandSolder
D5: 150120BS75000; LED_1206_3216Metric_Pad1.42x1.75mm_HandSolder
F1, F2, F3: 400mA; Fuse_0805_2012Metric_Pad1.15x1.40mm_HandSolder
J1: S10B-XH-A(LF)(SN); JST_XH_S10B-XH-A_1x10_P2.50mm_Horizontal
J2: Conn_01x05; connector_Harwin_M80-5000642
J3: Conn_01x05_Female; PinHeader_1x05_P2.54mm_Vertical
J4: Conn_01x05; PinHeader_2x03_P2.00mm_Vertical_MINISENSOR_Harwin_Spacing
J5, J6: M80-5000642; connector_Harwin_M80-5000642
J8: 693072010801; microSD_Molex_WM6698CT-ND
J11: Conn_01x05; PinHeader_2x03_P2.00mm_Vertical_Harwin_Spacing
L1: 33uH; L_1210_3225Metric_Pad1.42x2.65mm_HandSolder
L2: 18uH; L_Wuerth_HCI-1365
Q1: BSS138; SOT-23
Q3: AOD417; TO-252-3_TabPin2
R1, R2, R3, R12, R24: 10kR; R_0805_2012Metric_Pad1.20x1.40mm_HandSolder
R4, R5, R9: 500R; R_0805_2012Metric_Pad1.20x1.40mm_HandSolder
R6: 10kR; R_0805_2012Metric_Pad1.15x1.40mm_HandSolder
R7, R11: 66.25mR; R_1206_3216Metric_Pad1.30x1.75mm_HandSolder
R8: 86.6kR; R_0805_2012Metric_Pad1.20x1.40mm_HandSolder
R10: 100R; R_0805_2012Metric_Pad1.15x1.40mm_HandSolder
R13: 18.7kR; R_0805_2012Metric_Pad1.20x1.40mm_HandSolder
R14: 470kR; R_0805_2012Metric_Pad1.20x1.40mm_HandSolder
R15: 16.2kR; R_0805_2012Metric_Pad1.20x1.40mm_HandSolder
R16: 20R; R_0805_2012Metric_Pad1.20x1.40mm_HandSolder
R17: 330R; R_0805_2012Metric_Pad1.20x1.40mm_HandSolder
R18: 68kR; R_0805_2012Metric_Pad1.15x1.40mm_HandSolder
R19, R20: 68kR; R_0805_2012Metric_Pad1.20x1.40mm_HandSolder
R21, R23: 132kR; R_0805_2012Metric_Pad1.20x1.40mm_HandSolder
R22: 132kR; R_0805_2012Metric_Pad1.15x1.40mm_HandSolder
R25: 30kR; R_0805_2012Metric_Pad1.15x1.40mm_HandSolder
R26: 5kR; R_0805_2012Metric_Pad1.20x1.40mm_HandSolder
R27, R28: 0R; R_0805_2012Metric_Pad1.20x1.40mm_HandSolder
R29: 30k; R_0805_2012Metric_Pad1.20x1.40mm_HandSolder
R30: 10k; R_0805_2012Metric_Pad1.20x1.40mm_HandSolder
U1, U2: INA180A4QDBVRQ1; SOT-23-5_HandSoldering
U3: LM22678TJ-5.0; TO-263-7_TabPin4
U4: LDK320ADU120R; SOT-89-3_Handsoldering
U5: MCP2515-I/P; SOIC-18W_7.5x11.6mm_P1.27mm
U6: TPS61175QPWPRQ1; TPS61175_Q1_Footprint
U7, U10: MCP2562-E/SN; SOIC-8_3.9x4.9mm_P1.27mm
U8: DSPIC33EP512GP502; SOIC-28W_7.5x17.9mm_P1.27mm
U9: AP2114H-3.3TRG1; SOT-223-3_TabPin2
Y1, Y2: 12MHz; Crystal_HC49-4H_Vertical

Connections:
3V3_CURR_AMP: U2.1, U8.3
+3V3: C19.2, C20.1, J8.4, J11.1, Q1.1, R11.1, R12.1, U2.4, U9.2
+5.3V: C7.2, C17.2, C18.2, C21.2, J3.4, J4.2, J11.2, L2.2, R16.1, R25.1, R27.2, U1.5, U2.5, U9.3
+5V: R2.1, R3.1, R25.2, R26.1
+12V: C28.1, J4.1, U4.1
+BATT: C4.1, C5.1, C22.1, C27.1, J1.10, L1.1, R7.1, R7.2, R29.1, U1.3, U1.4, U3.2, U4.3, U6.3
/5.3V_OUT: J5.1, J6.1, R28.1
/5V3_ALWAYS_ON: C11.2, C12.1, C13.1, C14.1, C15.1, C16.1, C29.1, Q3.3, R1.1, R6.1, R24.1, R27.1, U5.17, U5.18, U7.3, U7.5, U8.13, U8.28, U10.3, U10.5
/+: J4.4, J11.4, U10.7
/-: J4.5, J11.5, U10.6
/CANH_ROCKET: J2.4, U7.7
/CANL_ROCKET: J2.5, U7.6
/ICSPCLK: J3.1, U8.6
/ICSPDAT: J3.2, U8.7
/Logger board/CS: R3.2, R18.2, U8.14
/Logger board/MISO: Q1.2, R2.2, U5.15, U8.17
/Logger board/MOSI: R19.2, U5.14, U8.18
/Logger board/SCK: R20.2, U5.13, U8.16
/MCU and CAN controllers/CAN_INT: U5.12, U8.21
/MCU and CAN controllers/CLKOUT: U5.3, U8.22
/MCU and CAN controllers/CS_1: R24.2, U5.16, U8.15
/MCU and CAN controllers/MCP_RX: U5.2, U7.4
/MCU and CAN controllers/MCP_TX: U5.1, U7.1
/MCU and CAN controllers/OSC1: C9.1, U8.9, Y1.1
/MCU and CAN controllers/OSC2: C10.1, U8.10, Y1.2
/MCU and CAN controllers/OSC3: C1.1, U5.7, Y2.1
/MCU and CAN controllers/OSC4: C2.1, U5.8, Y2.2
/MCU and CAN controllers/PIC_RX: U8.12, U10.4
/MCU and CAN controllers/PIC_TX: U8.11, U10.1
/PWR_EN: U3.7, U6.4, U8.4
/battery_management/3V3_OUT: R11.2, U2.3
/~MCLR: C3.1, J3.5, R6.2, R10.2
BATT_CURR_AMP: U1.1, U8.2
GND: C1.2, C2.2, C3.2, C4.2, C5.2, C7.1, C8.2, C9.2, C10.2, C11.1, C12.2, C13.2, C14.2, C15.2, C16.2, C17.1, C18.1, C19.1, C20.2, C21.1, C22.2, C23.2, C24.2, C25.2, C26.2, C27.2, C28.2, C29.2, D2.2, D3.1, D4.1, D5.1, J1.3, J2.3, J3.3, J4.3, J5.3, J6.3, J8.6, J8.9, J11.3, R8.2, R15.2, R17.1, R21.2, R22.2, R23.2, R26.2, R30.2, U1.2, U2.2, U3.4, U4.2, U5.9, U6.6, U6.7, U6.12, U6.13, U6.14, U6.15, U7.2, U7.8, U8.8, U8.19, U8.27, U9.1, U10.2, U10.8
MAMA_PWR_EN: Q3.1, R1.2, U8.26
unnamed: C6.1, D2.1, L2.1, U3.1
unnamed: C6.2, U3.3
unnamed: C8.1, U8.20
unnamed: C23.1, U6.5
unnamed: C24.1, R13.1
unnamed: C25.1, C26.1, D1.1, R14.1
unnamed: D1.2, L1.2, U6.1, U6.2
unnamed: D3.2, R9.2
unnamed: D4.2, R4.2
unnamed: D5.2, R5.2
unnamed: F1.1, J1.8
unnamed: F1.2, J1.9
unnamed: F2.1, J1.6
unnamed: F2.2, J1.7
unnamed: F3.1, J1.4
unnamed: F3.2, J1.5
unnamed: J8.2, R18.1, R22.1
unnamed: J8.3, R19.1, R23.1
unnamed: J8.5, R20.1, R21.1
unnamed: J8.7, Q1.3, R12.2
unnamed: Q3.2, R28.2
unnamed: R4.1, U8.24
unnamed: R5.1, U8.23
unnamed: R8.1, U6.10
unnamed: R9.1, U8.25
unnamed: R10.1, U8.1
unnamed: R13.2, U6.8
unnamed: R14.2, R15.1, U6.9
unnamed: R16.2, R17.2, U3.6
V_SENSE: R29.2, R30.1, U8.5

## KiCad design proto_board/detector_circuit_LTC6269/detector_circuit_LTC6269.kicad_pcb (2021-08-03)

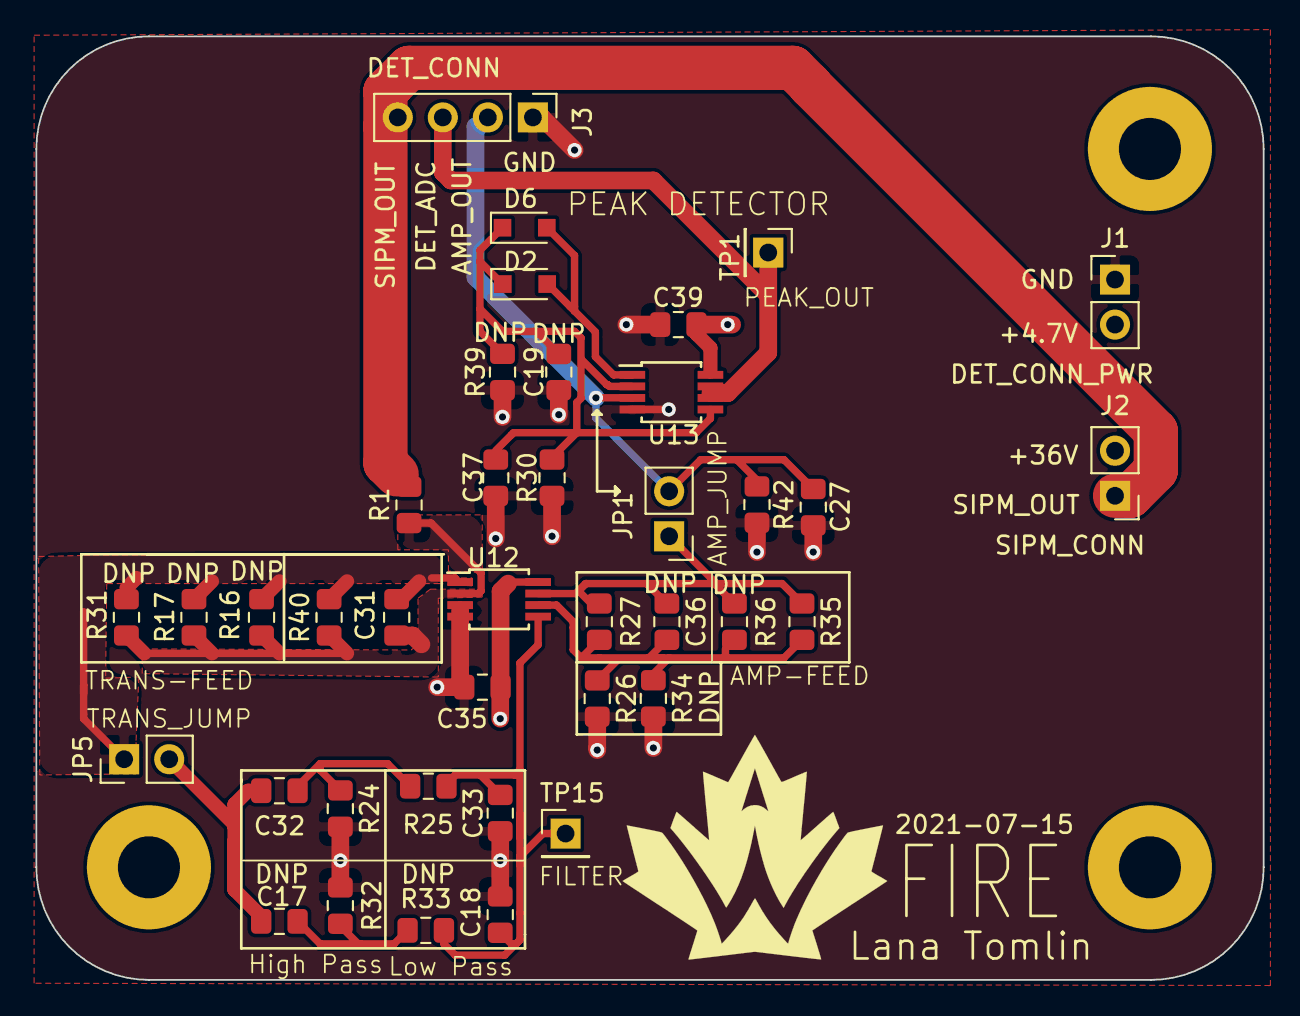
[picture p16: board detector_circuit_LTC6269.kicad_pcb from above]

Board: 4 copper layers, 69.2 x 53.2 mm, 39 parts (0 on the bottom side), 15 nets.

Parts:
C17, C18, C19: DNP; C_0805_2012Metric_Pad1.15x1.40mm_HandSolder
C27, C37: 2.2n; C_0805_2012Metric_Pad1.15x1.40mm_HandSolder
C31, C33: 1n; C_0805_2012Metric_Pad1.15x1.40mm_HandSolder
C32: 10n; C_0805_2012Metric_Pad1.15x1.40mm_HandSolder
C35, C39: 0.1u; C_0805_2012Metric_Pad1.15x1.40mm_HandSolder
C36: 470p; C_0805_2012Metric_Pad1.15x1.40mm_HandSolder
D2, D6: CUS08F30H3FCT-ND; D_SOD-323_HandSoldering
J1: DET_CONN_PWR; PinHeader_1x02_P2.54mm_Vertical
J2: SIPM_CONN; PinHeader_1x02_P2.54mm_Vertical
J3: DET_CONN; PinHeader_1x04_P2.54mm_Vertical
JP1: AMP_JUMP; PinHeader_1x02_P2.54mm_Vertical
JP5: TRANS_JUMP; PinHeader_1x02_P2.54mm_Vertical
R1: 1; R_0805_2012Metric_Pad1.15x1.40mm_HandSolder
R16, R17, R31, R32, R33, R34, R35, R36, R39: DNP; R_0805_2012Metric_Pad1.15x1.40mm_HandSolder
R24, R26: 100; R_0805_2012Metric_Pad1.15x1.40mm_HandSolder
R25, R40: 150; R_0805_2012Metric_Pad1.15x1.40mm_HandSolder
R27: 330; R_0805_2012Metric_Pad1.15x1.40mm_HandSolder
R30, R42: 1M; R_0805_2012Metric_Pad1.15x1.40mm_HandSolder
TP1: PEAK_OUT; PinHeader_1x01_P2.54mm_Vertical
TP15: FILTER; PinHeader_1x01_P2.54mm_Vertical
U12, U13: LTC6269; MSOP-8_3x3mm_P0.65mm

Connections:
+4.7V: C35.1, C39.1, J1.2, U12.8, U13.8
/AMP_OUT: C27.1, J3.2, JP1.2, R42.1, U13.3
/DET_ADC: J3.3, TP1.1, U13.6, U13.7
/Filter_IN: C17.2, C32.2, JP5.2
/SIPM_OUT: J2.1, J3.4, R1.2
GND: C18.1, C19.2, C27.2, C33.1, C35.2, C37.2, C39.2, J1.1, J3.1, R24.2, R26.2, R30.2, R32.2, R34.1, R39.2, R42.2, U12.3, U12.4, U13.4
unnamed: C17.1, R32.1, R33.2
unnamed: C18.2, C33.2, R25.1, R33.1, TP15.1, U12.5
unnamed: C19.1, C37.1, D2.1, D6.1, R30.1, R39.1, U13.2, U13.5
unnamed: C31.1, JP5.1, R16.1, R17.1, R31.1, R40.1, U12.1
unnamed: C31.2, R1.1, R16.2, R17.2, R31.2, R40.2, U12.2
unnamed: C32.1, R24.1, R25.2
unnamed: C36.1, JP1.1, R27.1, R35.1, R36.1, U12.7
unnamed: C36.2, R26.1, R27.2, R34.2, R35.2, R36.2, U12.6
unnamed: D2.2, D6.2, U13.1

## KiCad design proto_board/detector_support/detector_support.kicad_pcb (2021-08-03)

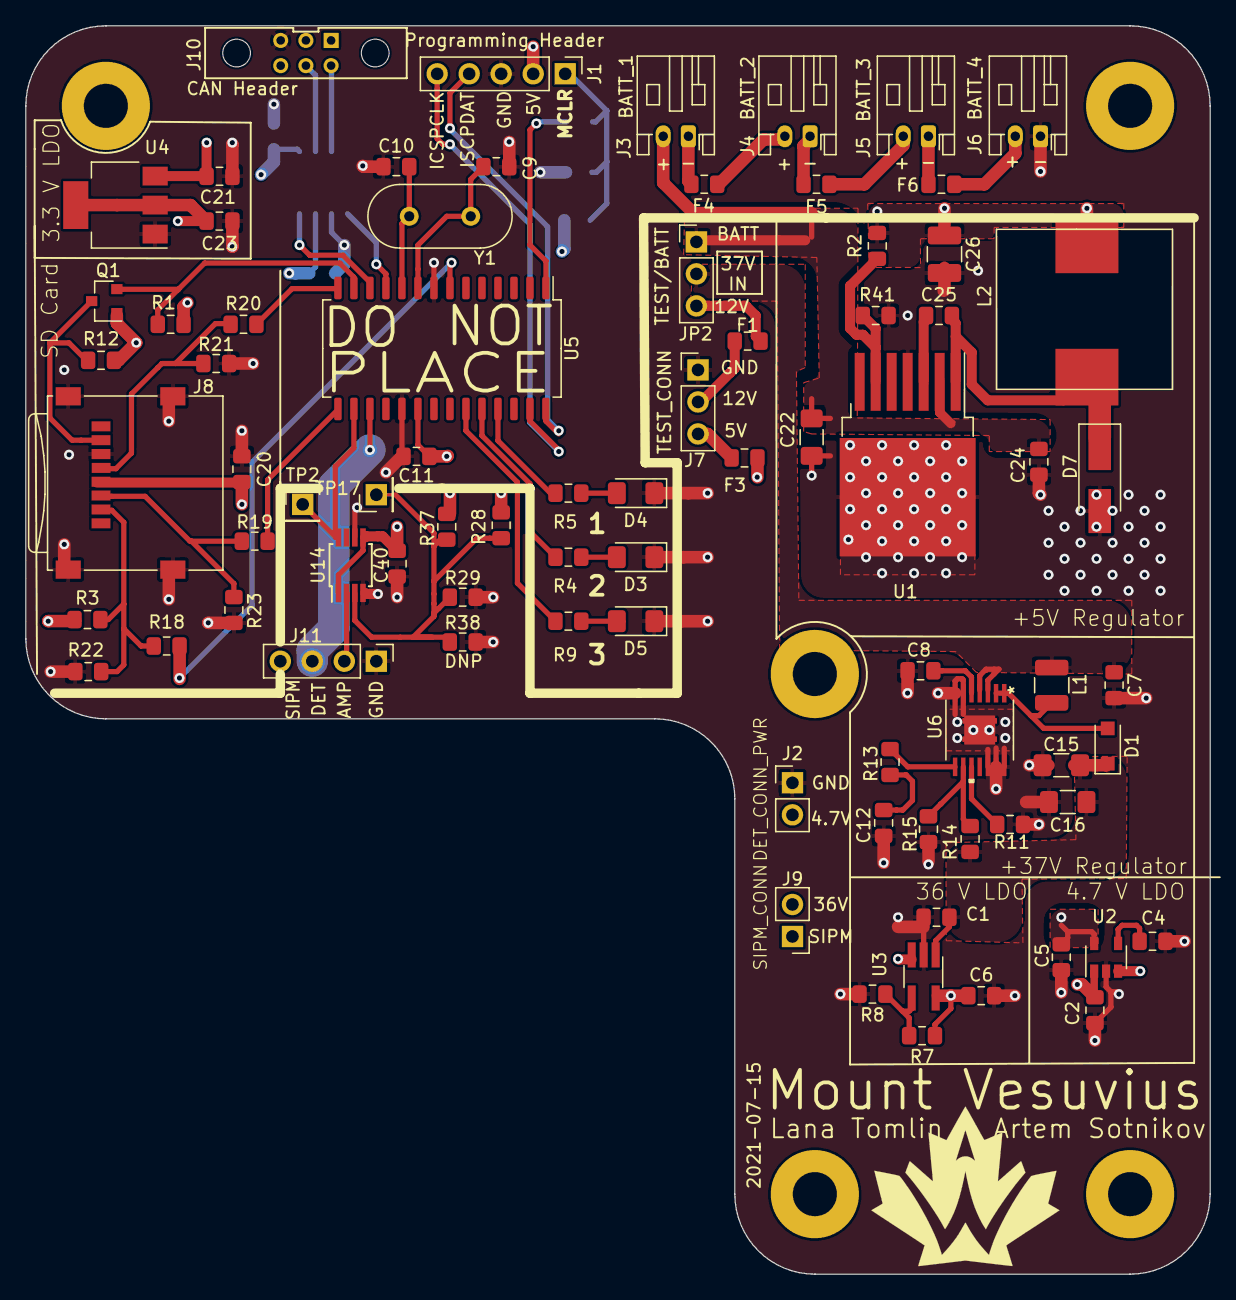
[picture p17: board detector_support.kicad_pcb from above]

Board: 4 copper layers, 94.0 x 99.1 mm, 86 parts (0 on the bottom side), 55 nets.

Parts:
C1, C2, C5, C21, C23, C24: 1u; C_0805_2012Metric_Pad1.15x1.40mm_HandSolder
C3, C40: 0.1u; C_0805_2012Metric_Pad1.15x1.40mm_HandSolder
C4, C25: 10n; C_0805_2012Metric_Pad1.15x1.40mm_HandSolder
C6: 0.5u; C_0805_2012Metric_Pad1.15x1.40mm_HandSolder
C7: 10u; C_0805_2012Metric_Pad1.15x1.40mm_HandSolder
C8: 47n; C_0805_2012Metric_Pad1.15x1.40mm_HandSolder
C9, C10: 26pF; C_0805_2012Metric_Pad1.15x1.40mm_HandSolder
C11, C13, C14: 0.1uF; C_0805_2012Metric_Pad1.15x1.40mm_HandSolder
C12: 1.5n; C_0805_2012Metric_Pad1.15x1.40mm_HandSolder
C15, C16: 10u; C_1206_3216Metric_Pad1.42x1.75mm_HandSolder
C20: 4.7uF; C_0805_2012Metric_Pad1.15x1.40mm_HandSolder
C22: 4.7u; C_1206_3216Metric_Pad1.42x1.75mm_HandSolder
C26: 56u; C_1210_3225Metric_Pad1.42x2.65mm_HandSolder
D1: 570mV 1a; D_SOD-123F
D3: 156120RS75000; D_1206_3216Metric_Pad1.42x1.75mm_HandSolder
D4: 150120BS75000; D_1206_3216Metric_Pad1.42x1.75mm_HandSolder
D5: QBLP650-IW; D_1206_3216Metric_Pad1.42x1.75mm_HandSolder
D7: D; D_SMA_Handsoldering
F1, F3, F4, F5, F6: 400ma; Fuse_0805_2012Metric_Pad1.15x1.40mm_HandSolder
J1: Programming Header; PinHeader_1x05_P2.54mm_Vertical
J2: DET_CONN_PWR; PinHeader_1x02_P2.54mm_Vertical
J3: BATT_1; JST_PH_S2B-PH-K_1x02_P2.00mm_Horizontal
J4: BATT_2; JST_PH_S2B-PH-K_1x02_P2.00mm_Horizontal
J5: BATT_3; JST_PH_S2B-PH-K_1x02_P2.00mm_Horizontal
J6: BATT_4; JST_PH_S2B-PH-K_1x02_P2.00mm_Horizontal
J7: TEST_CONN; PinHeader_1x03_P2.54mm_Vertical
J8: 693072010801; microSD_Molex_WM6698CT-ND
J9: SIPM_CONN; PinHeader_1x02_P2.54mm_Vertical
J10: Conn_01x06_Female; connector_Harwin_M80-5000642
J11: DET_CONN; PinHeader_1x04_P2.54mm_Vertical
JP2: TEST/BATT; PinHeader_1x03_P2.54mm_Vertical
L1: 33u; L_1210_3225Metric
L2: 15u; 732-3880-1-ND
Q1: BSS138; SOT-23
R1, R3, R10, R12: 10k; R_0805_2012Metric_Pad1.15x1.40mm_HandSolder
R2: 20; R_0805_2012Metric_Pad1.15x1.40mm_HandSolder
R4, R5, R9, R41: 330; R_0805_2012Metric_Pad1.15x1.40mm_HandSolder
R6: 100; R_0805_2012Metric_Pad1.15x1.40mm_HandSolder
R7, R28: 100k; R_0805_2012Metric_Pad1.15x1.40mm_HandSolder
R8: 3.5k; R_0805_2012Metric_Pad1.15x1.40mm_HandSolder
R11: 85.4k; R_0805_2012Metric_Pad1.15x1.40mm_HandSolder
R13: 18.2k; R_0805_2012Metric_Pad1.15x1.40mm_HandSolder
R14: 470k; R_0805_2012Metric_Pad1.15x1.40mm_HandSolder
R15: 16.2k; R_0805_2012Metric_Pad1.15x1.40mm_HandSolder
R18, R19, R20: 34k; R_0805_2012Metric_Pad1.15x1.40mm_HandSolder
R21, R22, R23: 66k; R_0805_2012Metric_Pad1.15x1.40mm_HandSolder
R29: 15k; R_0805_2012Metric_Pad1.15x1.40mm_HandSolder
R37, R38: DNP; R_0805_2012Metric_Pad1.15x1.40mm_HandSolder
TP2: INTERRUPT; PinHeader_1x01_P2.54mm_Vertical
TP17: COMP_BIAS; PinHeader_1x01_P2.54mm_Vertical
U1: LM22678TJ-5.0_NOPB; TO-263-7_TabPin4
U2: LD3985M47R_SOT23; SOT-23-5
U3: LT3014IS5#TRMPBF; TSOT-23-5_HandSoldering
U4: AP2114H-3.3TRG1; SOT-223
U5: PIC18LF26K83; SOIC-28W_7.5x18.7mm_P1.27mm
U6: TPS61175QPWPRQ1; TPS61175_Q1_Footprint
U10: MCP2562-E/SN; SOIC-8_3.9x4.9mm_P1.27mm
U14: LT1711xMS8; MSOP-8_3x3mm_P0.65mm
Y1: 12MHz; Crystal_HC49-4H_Vertical

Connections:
+3V3: C20.1, C23.1, J8.4, Q1.1, R3.1, R12.1, U4.2, U4.4
+4.7V: C5.1, J2.2, U2.5
+5V: C2.1, C11.2, C13.1, C14.1, C21.2, C26.1, C40.1, F3.1, J1.2, L2.2, R1.1, R2.1, R10.1, R28.1, R37.1, U2.1, U2.3, U3.3, U4.3, U5.20, U10.3, U10.5, U14.1, U14.5
+12V: F1.1, JP2.3
+36V: C6.1, J9.2, R7.1, U3.5
+37V: C1.1, C15.1, C16.1, D1.1, R14.1, U3.1
+BATT: C22.1, C24.1, J3.2, JP2.1, U1.2
/AMP_OUT: J11.2, U14.2
/DET_ADC: J11.3, U5.17
/INTERUPT_OUT: TP2.1, U5.16, U14.8
/Microcontroller [DO NOT PLACE]/CANH: J10.4, U10.7
/Microcontroller [DO NOT PLACE]/CANL: J10.5, U10.6
/Microcontroller [DO NOT PLACE]/CS: R18.2, U5.7
/Microcontroller [DO NOT PLACE]/ICSPCLK: J1.5, U5.27
/Microcontroller [DO NOT PLACE]/ICSPDAT: J1.4, U5.28
/Microcontroller [DO NOT PLACE]/MCLR: C3.1, J1.1, R6.2, R10.2
/Microcontroller [DO NOT PLACE]/MISO: Q1.2, R1.2, R19.2, U5.13, U5.15
/Microcontroller [DO NOT PLACE]/OSC1: C9.1, U5.9, Y1.1
/Microcontroller [DO NOT PLACE]/OSC2: C10.1, U5.10, Y1.2
/Microcontroller [DO NOT PLACE]/PIC_RX: U5.12, U10.4
/Microcontroller [DO NOT PLACE]/PIC_TX: U5.11, U10.1
/Microcontroller [DO NOT PLACE]/SCK: R20.2, U5.14
GND: C1.2, C2.2, C3.2, C4.2, C5.2, C6.2, C7.2, C8.2, C9.2, C10.2, C11.1, C12.2, C13.2, C14.2, C15.2, C16.2, C20.2, C21.1, C22.2, C23.2, C24.2, C26.2, C40.2, D3.1, D4.1, D5.1, D7.2, J1.3, J2.1, J6.1, J7.1, J8.6, J8.9, J10.3, J11.1, R8.2, R11.2, R15.2, R21.2, R22.2, R23.2, R29.2, R38.2, R41.2, U1.4, U2.2, U3.2, U4.1, U5.8, U5.19, U6.6, U6.7, U6.12, U6.13, U6.14, U6.15, U10.2, U10.8, U14.4, U14.6
unnamed: C4.1, U2.4
unnamed: C7.1, JP2.2, L1.2, U6.3, U6.4
unnamed: C8.1, U6.5
unnamed: C12.1, R13.1
unnamed: C25.1, D7.1, L2.1, U1.1
unnamed: C25.2, U1.3
unnamed: D1.2, L1.1, U6.1, U6.2
unnamed: D3.2, R4.2
unnamed: D4.2, R5.2
unnamed: D5.2, R9.2
unnamed: F1.2, J7.2
unnamed: F3.2, J7.3
unnamed: F4.1, J3.1
unnamed: F4.2, J4.2
unnamed: F5.1, J4.1
unnamed: F5.2, J5.2
unnamed: F6.1, J5.1
unnamed: F6.2, J6.2
unnamed: J8.2, R3.2, R18.1, R22.1
unnamed: J8.3, R19.1, R23.1
unnamed: J8.5, R20.1, R21.1
unnamed: J8.7, Q1.3, R12.2
unnamed: R2.2, R41.1, U1.6
unnamed: R4.1, U5.24
unnamed: R5.1, U5.25
unnamed: R6.1, U5.1
unnamed: R7.2, R8.1, U3.4
unnamed: R9.1, U5.23
unnamed: R11.1, U6.10
unnamed: R13.2, U6.8
unnamed: R14.2, R15.1, U6.9
unnamed: R28.2, R29.1, R37.2, R38.1, TP17.1, U14.3

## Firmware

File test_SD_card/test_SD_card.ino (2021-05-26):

#include <SD.h>

//Global vars
File diodeOutput;
File sipmOutput;
File voltage;

String file1 = "test4.txt";
String file2 = "test5.txt";
String file3 = "test6.txt";

volatile bool savefile = false;

void setup()
{
  //start serial
  Serial.begin(115200); // Baud Rate (Clock frequency for serial)

  //set pin to get
  pinMode(A1, INPUT);
  pinMode(A2, INPUT);
  pinMode(A0, INPUT);
  pinMode(3, INPUT);

  //setting CS pin to output
  pinMode(10, OUTPUT);

  if (!SD.begin(10))
  {
    Serial.println("SD card initialization failed!");
  }

  diodeOutput = SD.open(file1, FILE_WRITE);
  sipmOutput = SD.open(file2, FILE_WRITE);
  voltage = SD.open(file3, FILE_WRITE);

  // if the file opened okay, write to it:
  if (diodeOutput && sipmOutput && voltage)
  {
    Serial.println("SD okay");
  }
  // if file doesnt open okay then flash led on board and scream SD not okay (and try again)
  // TBD

  diodeOutput.println("testStarted");
  sipmOutput.println("testStarted");

  //SET-UP FOR YOUR TIMERS: (stolen from https://www.robotshop.com/community/forum/t/arduino-101-timers-and-interrupts/13072)
  // initialize timer1
  noInterrupts(); // disable all interrupts

  TCCR1A = 0;

  TCCR1B = 0;

  TCNT1 = 0;

  //https://ww1.microchip.com/downloads/en/DeviceDoc/Atmel-7810-Automotive-Microcontrollers-ATmega328P_Datasheet.pdf
  OCR1A = 6250; // compare match register 16MHz/256 Prescalar/10Hz
  // The value of OCR1A is determined by CPU frequency (16MHz), Prescalar value (1/256) and desired frequency
  // In other words, OCR1A is the maximum timer value (it needs to be less than 65536 (16bit timer) to prevent overflow)
  // By setting OCR1A = 6250, we get desired frequency of 10Hz

  TCCR1B = (1 << WGM12); // CTC mode (= because TCCR1B is 0 so its the same as |=)

  TCCR1B &= (0 << CS10); // 0
  TCCR1B &= (0 << CS11); // 0
  TCCR1B |= (1 << CS12); // 1

  TIMSK1 |= (1 << OCIE1A); // enable timer compare interrupt

  interrupts(); // enable all interrupts
}

ISR(TIMER1_COMPA_vect)
{
  //Interrupt Closes and reopens the files
  savefile = true;
}

const float DAC = 5.0 / 1023.0; //DAC conversion rate (Voltage/Bits)

void loop()
{
  float diode_val = analogRead(A1) * DAC;
  float sipm_val = analogRead(A0) * DAC;
  float voltage_val = analogRead(A2) * DAC;

  diodeOutput.print(millis());
  diodeOutput.print(" : ");
  diodeOutput.println(diode_val, 6);

  sipmOutput.print(millis());
  sipmOutput.print(" : ");
  sipmOutput.println(sipm_val, 6);

  voltage.print(millis());
  voltage.print(" : ");
  voltage.println(voltage_val, 6);

  if (savefile)
  { // Closes file and reopens it after interrupt
    savefile = false;
    diodeOutput.close();
    sipmOutput.close();
    voltage.close();

    diodeOutput = SD.open(file1, FILE_WRITE);
    sipmOutput = SD.open(file2, FILE_WRITE);
    voltage = SD.open(file3, FILE_WRITE);
  }
}

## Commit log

2019-11-09 Added KiCad files with IMU, SD Logger, and Arduino Nano
    [Experiment Board.kicad_pcb, Experiment Board.sch, LevelShifter.sch, SDLogger.sch]
2020-01-08 added MLB and SiPM board
    [Experiment Board.kicad_pcb, Experiment Board.sch, LevelShifter.sch, Payload2020_SIPM_board.kicad_pcb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]
2020-01-13 adding finished payload schematic layout
    [Altimeter.sch, CAN Power.sch, file5E13F8E8.sch, file5E163A2A.sch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]
2020-06-03 Modify folder names
    [Altimeter.sch, CAN Power.sch, Payload2020_SIPM_board.kicad_pcb, Payload2020_SIPM_board.sch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]
2021-01-01 Removed irrelevant files
    [Experiment Board.kicad_pcb, Experiment Board.sch, LevelShifter.sch, Payload2020_SIPM_board.kicad_pcb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]
2021-01-01 cleaned up files
    [payload2020_mama_board.kicad_pcb, payload2020_mama_board.sch]
2021-04-27 Added power management schematic
    Added power management, changed power management input voltage to 12V, and added new symbol to library.
    [payload2020_mama_board.sch, power_management.sch]
2021-05-01 Updated power management sheet
    Updated power management sheet, replaced LDO design with a boost converter
    [power_management.sch]
2021-05-07 Edited power management sheet
    [power_management.sch]
2021-05-07 Updated power management sheet, added missing PIC18 sheet
    [PIC18F26K83.sch, power_management.sch]
2021-05-08 Fixed 5V CAN connection
    Removed second 12V connector, replaced with 5V
    [payload2020_mama_board.sch]
2021-05-09 Moved power supplies to papa board, updated PDF
    Removed power management sheet, moved schematic to papa board
    [PIC18F26K83.sch, payload2020_mama_board.sch, power_management.sch]
2021-05-12 Made updated detector circuit - Needs a lot of clean up
    [PIC18F26K83.sch, detector_circuit.sch, payload2020_mama_board.sch]
2021-05-12 Added detector circuit with new op amp and configuration to mama, updated connections, added additional filtering for voltage supplies
    [detector_circuit.sch, payload2020_mama_board.sch]
2021-05-21 Moved 4.7V LDO from papa board to mama board, updated PDF
    [payload2020_mama_board.sch]
2021-05-22 Move 36V LDO from papa board to mama board, remove 4.7V and 36V filters, fix 4.7V and 36V power symbols, update PDF
    [detector_circuit.sch, payload2020_mama_board.sch]
2021-05-25 Add PIC18 and transceiver
    still needs connector to CAN bus
    [payload2020_mama_board.sch]
2021-05-25 Add low pass filters
    [payload2020_mama_board.sch]
2021-06-04 added a bunch of insfastructure so we can just use this straight up for drop test if the circuit works
    [SDcard.sch, detector_circuit.sch, pic_and_can_controllers.sch]
2021-06-05 Finished overall schematic - ERC errors that need to be fixed
    [SDcard.sch, detector_circuit.sch, pic_and_can_controllers.sch]
2021-06-06 Addressed Randy's comments
    [SDcard.sch, detector_circuit.sch, pic_and_can_controllers.sch, power_supplies.sch]
2021-06-06 fixed library references (hopefully)
    [detector_circuit.sch]
2021-06-06 2nd attempt at fixing libraries added missing values
    [detector_circuit.sch, power_supplies.sch]
2021-06-06 removed library reference in global library
    [detector_circuit.sch]
2021-06-06 Fixed things w/Zach's suggestions don't remember specifics, sorry
    [SDcard.sch, detector_circuit.sch, pic_and_can_controllers.sch, power_supplies.sch]
2021-06-09 assigned footprints started layout, still some footprint issues to fix
    [detector_circuit.kicad_pcb, detector_circuit.sch]
2021-06-11 Removed duplicate libararies - fixed power converter w/incorrect symbol
    [SDcard.sch, power_supplies.sch]
2021-06-11 Fixed symbol issues, assigned footprints
    [SDcard.sch, detector_circuit.sch, pic_and_can_controllers.sch, power_supplies.sch]
2021-06-11 Named connectors & test points, removed SIPM and added SIPM connector, added some more test points,fixed some symbols
    [detector_circuit.kicad_pcb, detector_circuit.sch, pic_and_can_controllers.sch, power_supplies.sch]
2021-06-12 Switched out +5V power supply, updated inductor footprints, fixed net label that was fucked, fixed some power control symbols i think im actually, finally, ready to start layout
    [detector_circuit.sch, power_supplies.sch]
2021-06-12 Grounded shield - thanks zachary
    [SDcard.sch]
2021-06-12 put in (hopefully) correct battery footprints, added board cut-out & randomly sized & placed holes, stared layout
    [SDcard.sch, detector_circuit.kicad_pcb, power_supplies.sch]
2021-06-12 layout mcksmayout
    [detector_circuit.kicad_pcb]
2021-06-12 finished ~papa board~ half of the layout
    [detector_circuit.kicad_pcb]
2021-06-13 Finished first version of layout, fixed some small mistakes on schematic
    [detector_circuit.kicad_pcb, detector_circuit.sch, pic_and_can_controllers.sch, power_supplies.sch]
2021-06-13 removed unecessary files
    [payload2020_mama_board.sch]
2021-06-13 re-did the entire papa board side of the layout cause,,,,,, i have poor time management skillz
    [detector_circuit.kicad_pcb]
2021-06-14 fixed up silkscreens, re-added detector circuit, added more labels
    [detector_circuit.kicad_pcb]
2021-06-14 Started routing - addressed like half of Dawson's comments, some of Chamath's comments
    [detector_circuit.kicad_pcb]
2021-06-15 fixed 5V regulator foot print, re-routed and started routing 36V regulator
    [detector_circuit.kicad_pcb, detector_circuit.sch]
2021-06-15 Restructure back layer layout
    Reshuffle the position of the comparator, peak detector, filter blocks. The new configuration should be easier to rout. Not much actual routing was done.
    [detector_circuit.kicad_pcb]
2021-06-15 did sm'ore routing, letting artem do some stuff :((
    [detector_circuit.kicad_pcb, payload2020_mama_board.kicad_pcb]
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2021-06-16 Fixed power symbols so they have a net, did more routing
    [detector_circuit.kicad_pcb, detector_circuit.sch, pic_and_can_controllers.sch, power_supplies.sch]
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2021-06-16 Finish Most of Routing
    - Power planes for 3.3, 4.7, 5 volts were created, along with high-power lines for the 36 and 37 volt sources.
    - Ground pours implemented on the front, plus an internal ground plane
    - inverting inputs on critical amplifiers isolated from any overlapping planes to kill capacitance
    - Almost everything fully routed
    The last part that remains to be done is some minor routing on the logger side. The MOSI/MISO issue is still haunting it, and it's late, so I will leave that for someone else to finish.
    Darn it's 2 am
    [detector_circuit.kicad_pcb]
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2021-06-20 Fixed some small silkscreen things, made mounting holes mounting holes
    [detector_circuit.kicad_pcb]
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2021-06-20 added missing connection and fixed 1 (1) weird trace length
    [detector_circuit.kicad_pcb]
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2021-06-27 Fixed some DRC issues
    [detector_circuit.kicad_pcb]
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2021-07-08 finished layout for testing infastructure, now detatchable from detector circuit for easy swappability
    [detector_circuit.kicad_pcb, detector_circuit.sch]
2021-07-09 1/3 swappable detector circuits layed out bbbyyy
    [detector_circuit_LTC6269.kicad_pcb, detector_circuit_LTC6269.sch]
2021-07-10 almost finished 2/4 of swappable detector circuits, im sorry i want to sleep. will continue the grind in the morning
    [detector_circuit_LTC6254.kicad_pcb, detector_circuit_LTC6254.sch]
2021-07-10 Finished 2nd swappable circuit layout
    [detector_circuit_LTC6254.kicad_pcb]
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2021-07-10 Fixedoverlapping copper areas & added name
    [detector_circuit_LTC6269.kicad_pcb]
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2021-07-13 Addressed Zachary's review, fixed some silkscreen issues and moved some components further apart. Added project information to README
    [detector_support.kicad_pcb]
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2021-07-13 Fix up detector board issues
    [SDcard.sch, detector_support.kicad_pcb, detector_support.sch, pic_and_can_controllers.sch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]
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2021-07-15 Added dates, fixed some small silkscreen issues generated final gerbers GOOD TO FUCKING GO
    [another_transimpedance_amplifier.sch, detector_circuit-B_Mask.gbr, detector_circuit-B_SilkS.gbr, detector_circuit-Edge_Cuts.gbr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]
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2021-09-30 Replaced comparator with AS393P-E1 comparator
    [comparitor_circuits.sch]
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2021-10-11 Annotate symbols, fix all ERC errors except one, update pdf
    [comparitor_circuits.sch, detector_circuit_LTC6269_2.sch, detector_circuit_LTC6269_3.sch, mama_board.sch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]
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2021-10-16 Finish routing, still need to fix DRC errors
    [mama_board.kicad_pcb]
2021-10-17 Fix DRC errors, finish silkscreen, update schematic pdf
    [mama_board.kicad_pcb, pic_and_can_controllers.sch]
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2021-11-18 Implement PCB review changes, fix mismatched trace widths
    [mama_board.kicad_pcb]
2021-11-19 Minor fixes, improve via placement
    [mama_board.kicad_pcb]
2021-11-25 Minor fixes, generate gerbers, update PDF
    [mama_board-B_Cu.gbr, mama_board-B_Mask.gbr, mama_board-B_Paste.gbr, mama_board-B_SilkS.gbr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]
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2022-01-15 Add date to silkscreen, fix copper pours, update gerbers
    [mama_board-B_Cu.gbr, mama_board-B_Mask.gbr, mama_board-B_Paste.gbr, mama_board-B_SilkS.gbr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]
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

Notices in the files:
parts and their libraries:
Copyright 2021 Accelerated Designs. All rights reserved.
